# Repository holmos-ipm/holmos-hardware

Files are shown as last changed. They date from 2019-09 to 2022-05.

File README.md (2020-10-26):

# Holmos - Hardware

Holmos is a digital holographic microscope.
The [software repository](https://github.com/holmos-ipm/holmos-rpi/) has more information about the project.

This repository contains instructions to build your own copy of the setup, and files describing the 3D-printed parts.

Unfortunately, shipping or selling kits is too complicated for our institute, so we cannot offer kits.

## Requirements

### Purchased parts
See [shopping list](shopping_list.md).
The steel rods need to be at least 600 mm long if you are using the reference design.

### Download; what to print
Unless you want to modify things, you can download .STL files directly from the `reference_assembly` subfolder [here](reference_assembly/).
Your printer's software should be able to read them directly.
Print one of each file, and you'll have everything you need.

If you are using parts with different diameters than the reference_assembly, modify the printable parts accordingly.

We developed this using Ultimaker printers and their [Cura](https://ultimaker.com/en/products/ultimaker-cura-software) software,
but any other printer should work.

### Assembly
Start by looking at `reference_assembly.py`.
It contains a list of parts, and their `z` positions along the optical axis.
Run the file, and it will generate a scad file showing the entire assembly (except rails).
In addition, a folder full of the individual parts is generated.
Print those parts, and assemble them at the positions given, and you should have a good starting point.

For instructions on individual parts, e.g. how to mount purchased parts in the printed mounts, see the [instructions folder](instructions).

### Adjustment, Usage
See [instructions/adjustment.md]() in this repository, or browse the [German student documentation](https://github.com/holmos-mikroskop/holmos/wiki)

### Optics Design
[instructions/optics_design.md]() explains the optics design in some more detail. 
You can probably skip this if you just want to use the microscope. 

## Optional parts
### Stability
Additional struts and crosses (e.g. Rpi_mount) can make the cage more stable.

### Light shield
A `round_mounts.round_mount_light(20, opening_angle=0, cyl_length=40, ring_thick=2)` can help shield the camera against stray light and make the setup work better in bright environments.

### Transport
The cage-based setup fits inside a tube (HT DN90).
To keep the setup from hitting the tube sides, print some `cage.cage_circumference()`
In a DN90 tube, the Raspberry Pi needs to be removed, and the movable mirror needs to be removed from the crane.
It can be stored in a `crane_mirror(mirror_offset_x=0, crane_only=True)` for transport.

## Tweaking
How tight the clips become depends on your printer, printer settings and the rods you are using.
`base.test_rod_clamp_tightness()` can be used to generate a test object with several clips.
Edit `Rods6mm_tightness` in `global_settings.ini`to change the fit globally.

## Modifying the 3D parts
To modify the parts, you'll need to compile from Python to SCAD to STL:

To re-create all parts, run
```
python reference_assembly.py
```
Be aware that this might take a long time (more than an hour) depending on the resolution you choose in OpenSCAD. You can install the required python packages with `pip3 install -r requirements.txt`. Also, make sure you have OpenSCAD installed in the location specified in `global_settings.ini`

To get scad files:
* A clone of this repository
* Python (only tested for python 3)
* [Solidpython](https://solidpython.readthedocs.io/en/latest/) - usually available through `pip install solidpython`

To convert from scad to stl:
* [OpenSCAD](http://www.openscad.org)

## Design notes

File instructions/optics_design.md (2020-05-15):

# HolMOS  Optics Design
Why are the optics arranged as they are?
There are reasons for many of the details in the HolMOS design.
Understanding the optics may be rewarding in itself, but it can also help in using and debugging the setup.

For an explanation of what to do to adjust an actual setup, [adjustment.md]() may be more helpful. 

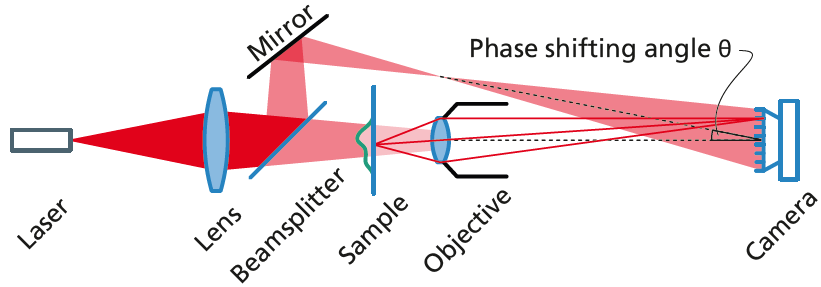
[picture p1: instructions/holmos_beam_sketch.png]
Sketch of the components and beams in Holmos


## Laser, condensor lens
The laser is used without its collimation lens, so that it emits a divergent cone of light.
This makes adjustment easier: we only care about the (x,y) position of the point-like source.
If the laser is at a slight angle, the cone still hits most of the lens.
A collimated, line-like beam would be very sensitive: 
  a slight change in angle would make it miss whatever it was pointed at.

The condensor lens creates a beam converging into the objective, illuminating the sample from many angles.
Wikipedia explains why focusing your illuminating light into the objective is good: [Köhler illumination](https://en.wikipedia.org/wiki/K%C3%B6hler_illumination).

## Sample, objective, camera
This part of the beam behaves like a classical optical microscope.
Note that the RPi camera has tiny 1.12 µm pixels and a 4.6 mm diagonal.
Common microscopes use ~20 mm image diameter, so there is quite a mismatch here. 
This has two consequences:
* Magnification numbers are confusing: 
  Magnification appears stronger with the RPi than when using the same objective with an eyepiece. 
  With a "10x" objective, a 460 µm region of the sample is imaged onto the camera.
* Objectives are diffraction limited, not being designed to resolve such tiny pixels.

## Reference beam: beamsplitter, mirror
### Phase shifting angle θ<sub>
To make this into an interferometer, an undisturbed reference beam is superimposed on the image.
If there is no sample, both waves are undisturbed.
In this case, the interference pattern is a set of bright/dark fringes filling the entire camera chip.
The spatial frequency k<sub>fringe</sub> is given by the wavelength λ and the angle θ between the beams:
> k<sub>fringe</sub> = θ / λ

(...using lazy-physicist-maths: sin(x)=tan(x)=x and angles are fractions of 2π instead of 360°, see [Radian](https://en.wikipedia.org/wiki/Radian))

The fringes need to be resolved by the camera.
A pattern of one light and one dark pixel can barely be resolved, known as the [Nyquist frequency](https://en.wikipedia.org/wiki/Nyquist_frequency).
This is also the spatial frequency that corresponds to the edges of the FFT:
> k<sub>max</sub> = 1 / 2px 

Combining this, the angle that gives a barely resolvable interference pattern is:
> θ<sub>max</sub> = λ / 2px

For a red laser (λ = 633 nm) and the RPi camera (px = 2 * 1.12 µm, using only the red pixels):
> θ<sub>max</sub> = 0.14

In reality, the diffraction order is not a point, but an area, so we want the actual angle to be smaller.
Ideally, a section through the FFT looks like this:
```
-k_max    -θ             0            +θ    +k_max
   |       |             |             |       |
   |....*******....XXXXXXXXXXXXX....*******....|
        -diff           DC           +diff
```
The`DC` term that is always present, even from the object beam by itself.
The two `diff`raction orders appear as soon as interference happens.

The position of the diffraction terms is given by the angle θ.
Converting the aperture size of the objective to an angle gives the width of the diffraction terms.
The DC term is twice as large as the diffraction orders.

To make everything fit nicely into the FFT, the optimum angle is θ<sub>opt</sub> = 3/4 * θ<sub>max</sub> = 0.11.

The current reference design uses a slightly larger value, θ = 35mm / 300mm = 0.12. 
That is still well below θ<sub>max</sub>, but makes getting the beam past the objective easier in real life.

### Reference beam focus
The object beam is not a plane wave when it arrives at the camera, not even if there is no object.
Imagine the objective had a very tiny aperture, like a pinhole camera: 
  the entire object beam comes from inside this aperture, so the wavefronts are cirular.
  
Although the angles are small due to the small camera chip, it is nice to have a flat phase image.
To achieve this, the reference beam needs to have the same curvature when the beams interfere:
  the entire reference beam should come from a single point that is the same distance from the camera as the objective.
Luckily, the condensor lens creates a focus in the reference beam - this focus should be roughly next to the objective.

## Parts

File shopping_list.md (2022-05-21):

# Shopping List

Links to shops with low-cost components tend to not last very long.
Often, the exact same items are available from different distributors, so try a search engine.
If you find something that works, please consider updating/adding a link here.

## Electronics
The links are pretty stable, but you might be able to find cheaper sources.

* Raspberry Pi 3B+ [35€ 3B+, RS](https://de.rs-online.com/web/p/entwicklungskits-prozessor-mikrocontroller/1373331/)
* RPi Camera v2 noIR [25€ RS](https://de.rs-online.com/web/p/videomodule/9132673/)
* SD card for the operating system

The code should work on other RPis as well.

Using a different camera is more complicated. 
If the pixel pitch is the same (2 * 1.12 µm from one red pixel to the next), you only™ need to change the code to use your camera.
To use a camera with different pixel pitch, read and understand the [optics design](instructions/optics_design.md).
You'll need to adjust the hardware as well.

## Mechanics
* 3D-Print (PLA) less than 10€ material costs.
* M3x10 7 pcs, 3 Nuts
  * 4 pcs for RPi (M3 pretty tight in some boards...)
  * 3 pcs and nuts for round mounts
* M2.5x4 4 pcs for the camera mount
* Steel rods 3Stk, 6mm*1m [15€ Hornbach](https://www.hornbach.de/shop/Rundstange-Edelstahl-6-mm-1-m/7813904/artikel.html)

## Optics
### Objective
The reference design uses a 4x objective lens from 
[55 € edmund optics](https://www.edmundoptics.de/p/4x-din-achromatic-commercial-grade-objective/5381/)

There are cheaper sources (sometimes with very similar quality), but using lower quality here can really hurt.
You can use different lenses by changing the diameter of the mount.
Keep in mind that the reference beam passes close to the objective: objectives with larger housings will block the beam.

### Condensor lens
An f=100 mm, d=25.4 mm lens is in the reference design, but similar lenses work with changes to the distances.
Adjust the mount diameter to fit your lens.
Using less than ~ 10 mm diameter will degrade the optical quality of you microscope.
  * There is a great lens, a real glass achromat, that is available in different webshops, usually specified as f~=99, d=26, e.g. [here 4,90€](hhttps://pgi-shop.de/achromat-linse-oe-26-0-mm-f-99-6-mm/)
  * Polymer lenses work, too.
  * (f=80mm, d=20mm [25€ edmund](https://www.edmundoptics.com/p/200mm-dia-x-800mm-fl-uncoated-plano-convex-lens/5903/))
  
### Beamsplitter: 
A "Teildurchlässiger Vorderflächen-Glasspiegel, 30 x 40 mm" keeps popping up in educational shops, e.g. 
[here 6,90€](https://pgi-shop.de/teildurchlaessiger-vorderflaechen-glasspiegel-30-x-40-mm/).

40 mm width is needed for the clip. 
These flat metal-on-glass beamsplitters work very well, and 50:50 is perfectly fine.
The front (i.e. coated) side faces the laser.

### Mirror
Use a front surface mirror for the reference beam. 
A "Vorderflächen-Glasspiegel, 22,0 x 15,5 mm" is usually available in german webshops, e.g.
[2,90 € here](https://pgi-shop.de/vorderflaechen-glasspiegel-22-0-x-15-5-mm/)

### Laser
We have used dd635-1-512x342 or DOE-QD650-0.4-12-10-22 from [Laserfuchs](https://www.laserfuchs.de]) (Their links go out of date quickly, though...).
 * It needs to be uncollimated, emitting a divergent beam:
    * Very cheap lasers come with glued-on lens. These can be removed with force/axes/saws/..., but you risk damaging the laser.
    * Some moderately cheap lasers (see above) come with a screw-in lens that can be removed easily.
 * No need for power, you are shining straight into the camera. Do your eyes a favor and use a Class 1 Laser.
 * Small laser modules with 5V input can be powered from a RPi USB port 
 * Adjust the mount diameter to fit your laser.

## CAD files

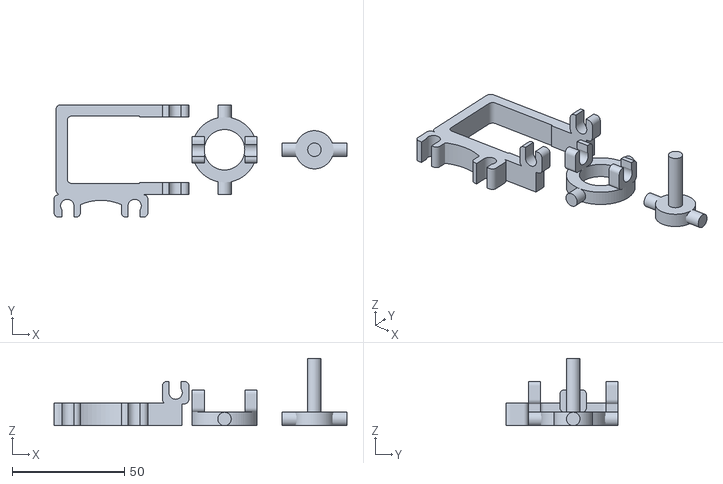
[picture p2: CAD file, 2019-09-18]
reference_assembly/06 - crane_mirror.stl
130.4 x 50.0 x 30.0

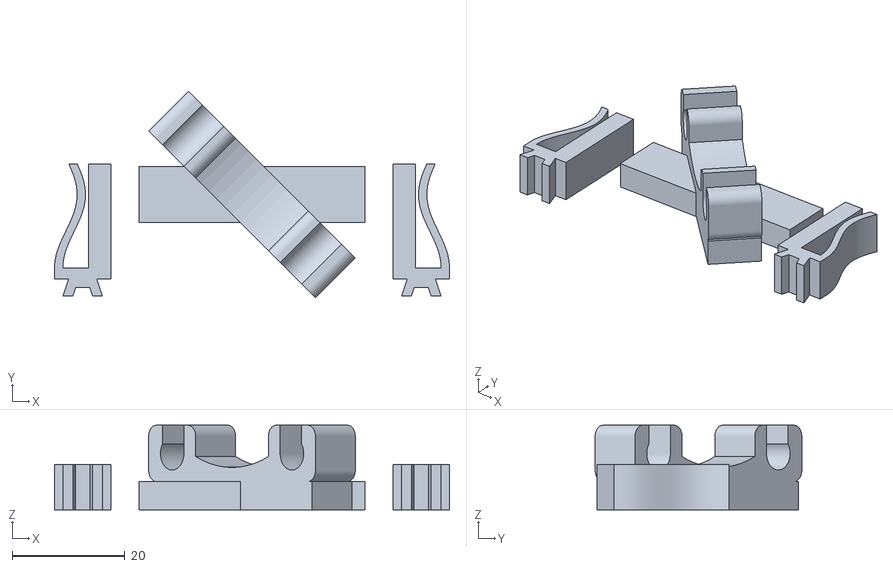
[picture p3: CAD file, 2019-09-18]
reference_assembly/05 - beamsplitter_mount.stl
70.0 x 36.6 x 15.0

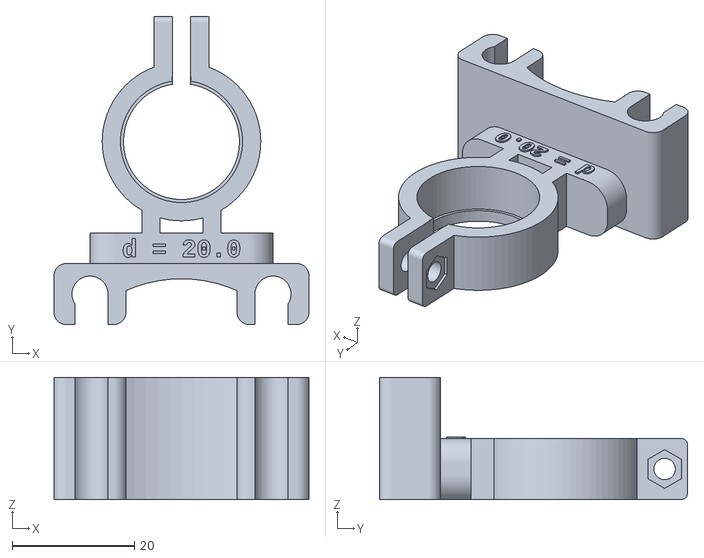
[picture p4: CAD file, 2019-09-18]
reference_assembly/03 - objective_lens_mount.stl
41.8 x 50.5 x 20.0

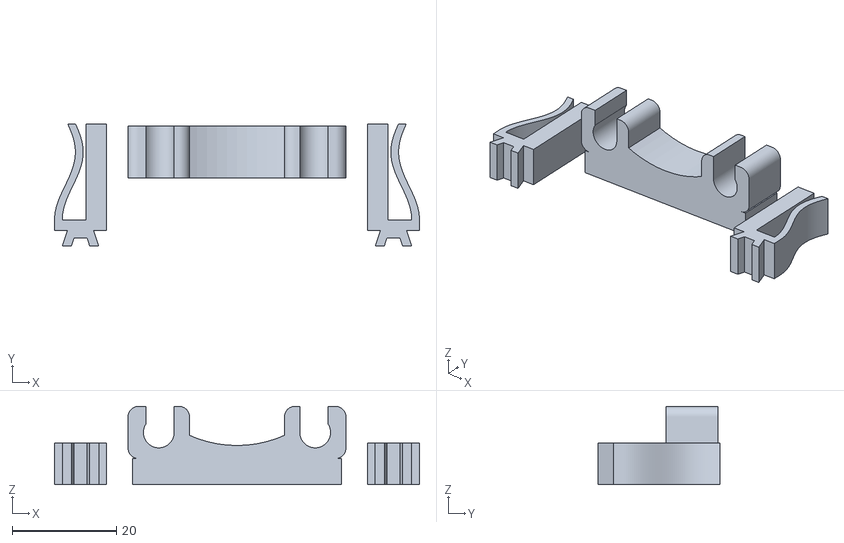
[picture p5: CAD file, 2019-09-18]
reference_assembly/04 - slide_holder.stl
70.0 x 23.4 x 15.0

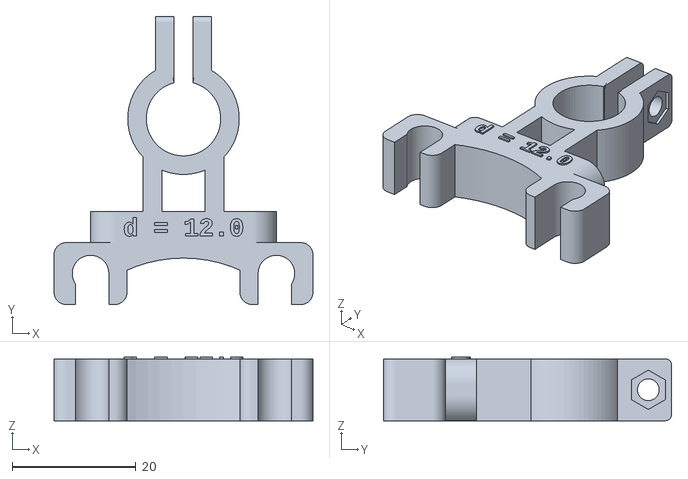
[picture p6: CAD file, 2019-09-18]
reference_assembly/09 - laser_mount.stl
41.8 x 46.5 x 10.2

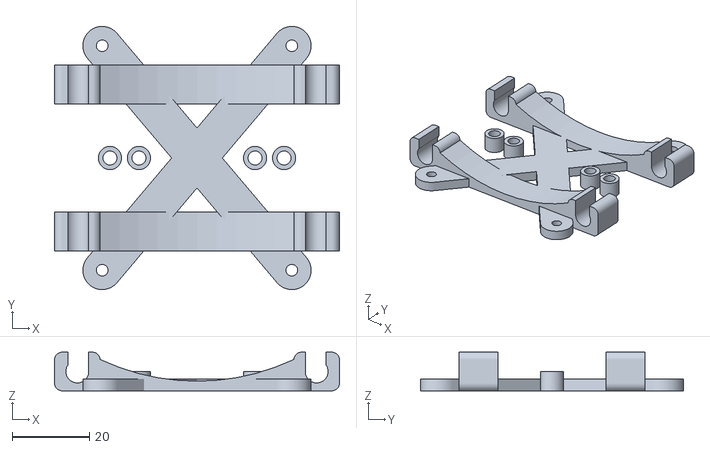
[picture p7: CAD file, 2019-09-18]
reference_assembly/02 - rpi_mount.stl
73.6 x 68.0 x 10.0

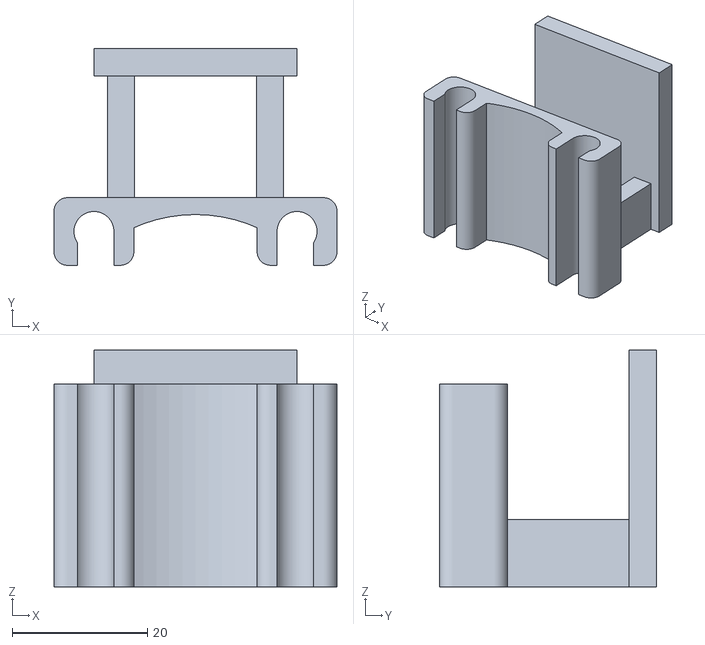
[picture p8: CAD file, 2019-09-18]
reference_assembly/08 - board_hook.stl
41.8 x 32.0 x 35.0

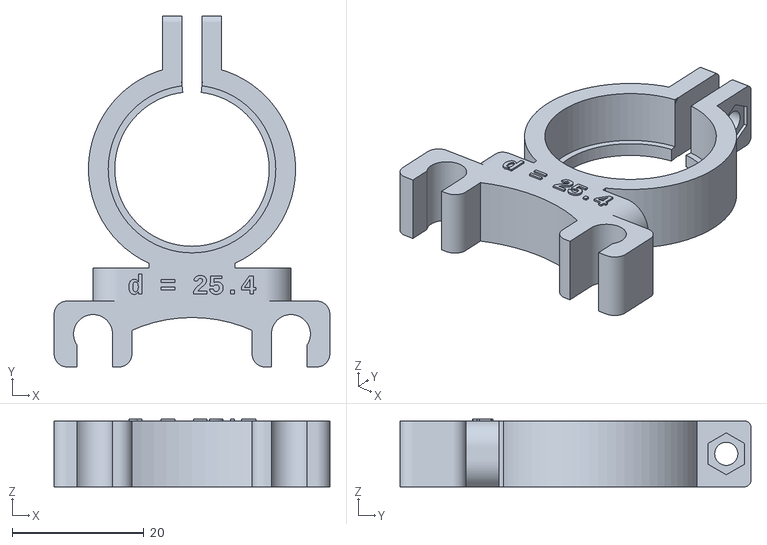
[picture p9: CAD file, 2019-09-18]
reference_assembly/07 - condensor_lens_mount.stl
41.8 x 53.2 x 10.2

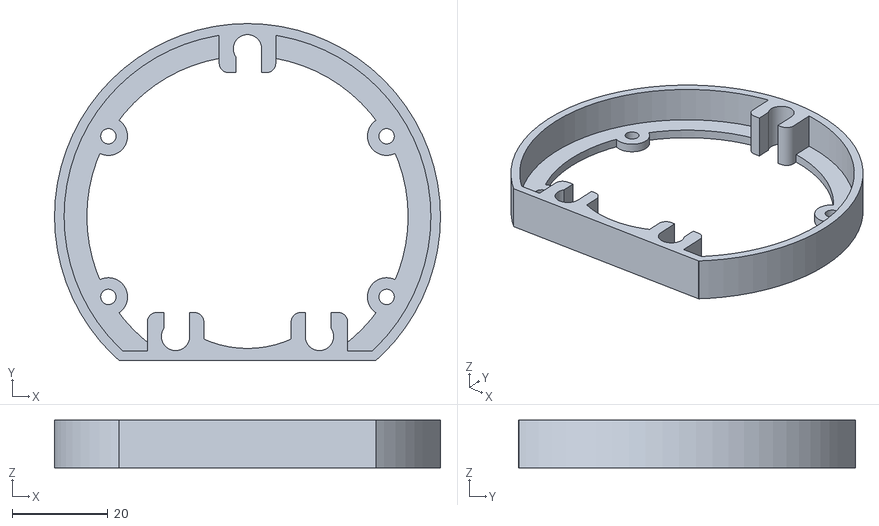
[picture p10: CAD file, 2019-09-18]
reference_assembly/00 - cage_circumference.stl
80.5 x 70.2 x 10.0

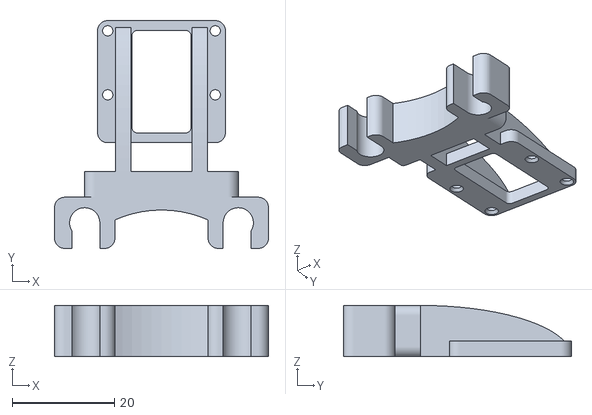
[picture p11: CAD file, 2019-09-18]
reference_assembly/01 - rpi_cam_mount.stl
41.8 x 44.5 x 10.0

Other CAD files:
reference_assembly/10 - cage_circumference.stl

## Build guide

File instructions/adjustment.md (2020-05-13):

# Adjusting a HolMOS microscope
This text tells you what to do; for a deeper understanding of _why_, see [optics_design.md]()

Start by putting everything at the positions given in [reference_assembly.py](../reference_assembly.py).
If you are using the recommended parts, that should be a very good starting position.

Sketch of the components and beams in Holmos

There are no thin, collimated beams anywhere in the setup. 
Remove the collimating lens from you laser, if there is one.
The beams in the sketch are not to scale, but give a good idea of what is going on.

The diverging beam from the laser may be larger than the condensor lens.
There is ample laser power, so we can waste some light here. 
Usually, the laser diode will not emit a round beam, but a highly elliptical one.
In its smaller dimension, the beam should fill the entire condensor lens.

Passing the sample, the beam has about 1 cm diameter.
It should fill the entire aperture of the objective, focussing at a point somewhere inside the objective.
At the camera, the "beam" will be much larger than the camera chip.

Move the sample (or the lens) until it is in focus.
It can be helpful to use the fast `raspistill -f` for this, instead of getting only a few frames per second in our gui.

The beamsplitter should have its coated side facing the laser. 
As in the sketch, the reference beam should have a focus approximately next to the objective.
To change where this focus is, move the laser.
Adjust the mirror so that the reference beam illuminates the entire camera chip.
It's ok if parts of the reference beam hit the sample or objective holder, as long as the camera chip is fully lit.

Block the reference beam to focus or to find your way around the sample.
It will be brighter than the object beam, making the object hard to see.
This is perfectly fine for interferometry, even if that may not be intuitive.

Now, using the holmos software, the FFT should have a bright point in the center,
 and two symmetrically spaced points near the edges.
Those points are due to interference of object and reference beam, and correspond to the +-1st diffraction orders: 
If you cover the reference beam, the two points should disappear.
As soon as a sample is in the object beam, the points should be surrounded by elliptical discs.
The software shows a rectangle with a center spot: the disc's diameters should match the rectangle's size.

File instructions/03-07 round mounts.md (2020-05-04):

The objective, the condensor lens and the laser are mounted into similar round mounts.
If you are using parts with different diameters than the reference_assembly, modify the printable parts accordingly.

The lens and objective mounts have a little ridge inside, so there is a correct, easy side to insert the lens from.

The mounts will probably be tight enough to keep the parts from falling out, but an M3x10 screw and a hex nut can be use to really tighten the clamp.
If you plan on moving the setup a lot, using the screw is a really good idea.

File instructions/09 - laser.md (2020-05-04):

For physical mounting, see [03-07 round mount.md]()

Unscrew the lens from the laser, we need a divergent beam.
There may be a tiny screw in the side of the laser, near the lens.
After loosening this screw, the lens is easy to turn.
Warning: The lens thread may be greased.

Please make sure your are allowed to operate the laser, and familiarize yourself with basic laser safety.
The laser we suggest is a class 2 laser, and by removing the lens, it becomes divergent.
We think this makes the device even safer, but cant guarantee this.
Put the supplied yellow safety sticker somewhere on the device.

The laser can be powered from a USB port - and the RPI has some.
You can simply cut open and old USB cable.
Usually, there will be four wires inside: black, red, and two other colors.
Solder the black (ground) and red (+5V) wires to the same colors on the laser.

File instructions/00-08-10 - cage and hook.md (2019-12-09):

The reference assemly uses two `cage.cage_circumference` at the ends to keep everything together.
You can use additional parts to make the setup even more rigid.

The `cage.board_hook()` can be used to hang the setup from a wall instead of mounting it to a surface.
Adjust `hook_opening` to fit the thickness of the wall/door/... you are hanging the setup from.
The flat faces on the `cage.cage_circumference` ensure that the setup rests against the wall.

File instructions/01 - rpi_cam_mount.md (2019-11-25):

Remove the tiny objective from the camera.
Usually, a tool is included to turn the objective: if you unscrew the objective far enough, it will fall out.

Fasten the camera to the smooth wide of the printed part, with the camera facing _into_ the rectangular hole in the part.
The flat cable should point towards the clips, so that the edges of the camera board match the printed rectangle.
Use four screws (M2.5 or M2.3).

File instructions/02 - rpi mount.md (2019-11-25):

Screw RPi to mount using four screws.
Use the four spacers (part of the printed file) to keep the wires on the back of the RPi from touching the mount.
That would bend the RPi when you tighten the screws.

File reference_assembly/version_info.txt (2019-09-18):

git info for ../holmos-hardware:
Revision v1.0-11-g3a60732
...with no changed files.

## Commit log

2018-08-01 Current objects, all in one file all four objects appear to render fine in Winpython64 3.6.3.0
2018-08-01 First shot at tiltable mirror mount
2018-08-02 Owis-"Threads" to position without intersections -> print like this running.
2018-08-09 TSe idea: front of mirror mount with three (leaf) springs
2018-08-10 Leaf springs separated from mount - print oriented such that spring is simple extrusion (#2)
2018-08-10 More stable plate, larger springs.. printing. #2
2018-08-10 Thicker springs.
2018-08-15 Parralel bar springs can be even longer.
2018-08-16 Tapered pins for easier insertion #2
2018-08-16 Since nuts are pressed in anyways: larger through-holes for screws.
2019-01-02 Objective mount uses opening angles; diameters are parameters.
2019-01-02 round_mount with clamps.
2019-01-04 - New method for creating an objective mount implemented - STL rendering disabled
2019-01-08 round_mount extended by inner stop_inner_diam (e.g. to mount lens)
2019-01-08 deleted solid-block objective mount; lightweight clamp is better.
2019-01-09 Clamp works fine as Objective Mount; Successfully printed lens mount and objective mount like this.
2019-01-09 Added mount for parallel rods (#3); Set this from global config. Refactor some things to helpers.py or base.py
2019-01-09 threads in cage holder
2019-01-09 * add X-shaped mount for Rpi * Add 45°-Mode (or other angles) to use slide_holder for beamsplitter * stabilizer_plate strongly refactored * render_stl.py created as separate file.
2019-01-10 added clamp_stabilizer and clamp_base_plate
2019-01-10 Temporary mount for existting 45° mirror to quickly test rod setup.
2019-01-10 -removed base_plate and stabilizer_plate -renamed clamp_* to cage_*
2019-01-10 added tube_with_rodmount
2019-01-10 created experimental all-plastic mirror mount.
2019-01-11 round_mount_light with new param cyl_length to make longer tubes; cyl_arc now supports edge case of full cylinder ;)
2019-01-16 Rpi mount now clamps to diagonals if using rods made distance to third rod gobally accessible in base.rods30...
2019-01-16 removed old mirror mount experiments; new version works well.
2019-01-16 Reorganize slide holder for printing in z-direction
2019-01-16 Added reference assembly
2019-01-18 assemble=bool kwarg for "final" parts -> bom and assembly from same func
2019-01-18 Holes in rpi_mount pass all the way through - no support structure generated by cura
2019-01-30 Fix: lens mount was returning nothing if assemble==True
2019-01-30 Alternate lasers and objective lenses
2019-01-30 Camera mount: Gap in central plate to allow mounting pcb on camera-side ...no more spacers needed, and saves printing volume.
2019-04-26 Fix circular import after move, rpi_mount clamps shifted to allow screwing from bottom -> display.
2019-05-08 Rename hole23 to sunk_hole, print RPi_mount with larger holes to use with nuts and display.
2019-05-14 Thinner light-shield tube; README += optional parts: hook, shield.
2019-05-15 Move cage_stabilizer() to inside-mounted orientation, center and enlarge aperture, refactor: extract cage_clips() for further use.
2019-05-15 cage.cage_circumference() for transport in tube
2019-05-16 clip on round_mound_light to +y - never blocks ref beam, even flipped Longer clips on objective mount: that's a heavy part.
2019-05-17 ADD: alternative laser
2019-09-17 simplify ref assembly: always use two "cage_circumference"; sort components
2019-09-17 cage_circumference: add holes for screws -> now all-purpose cage
2019-09-17 slide_holder: put clamps closer, so that parts are connected by skirt (...if printed with skirt)
2019-09-18 print git info to output dir, so that we can put stl into the repo and know when it was compiled
2019-09-18 print git info to output dir, so that we can put stl into the repo and know when it was compiled. Rename paths, identical to .py filename: reference assembly.
2019-09-18 Add stl files; add info to readme about those stl files.
    [00 - cage_circumference.stl, 01 - rpi_cam_mount.stl, 02 - rpi_mount.stl, 03 - objective_lens_mount.stl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]
2019-12-09 Refactor: round_mount_light() moved to round_mounts.py (formerly lens_mounts.py) Added docstring, now uses cube as slit instead of opening angle
2020-02-28 Mount for hexagonal high-power LEDs
2020-05-04 shopping_list.md: Expand laser specs so people can find alternatives (#1)
